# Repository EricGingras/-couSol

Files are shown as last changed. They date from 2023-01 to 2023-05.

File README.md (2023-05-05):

# Écou-Terre

**Déscription du projet:** Nous sommes en train de concevoir un module qui peut capter les bruits émis par les vers de terre, offrant ainsi une perspective sur la biodiversité et la santé des sols.  Ceci est le répertoire git de tous les fichiers techniques pour notre projet.

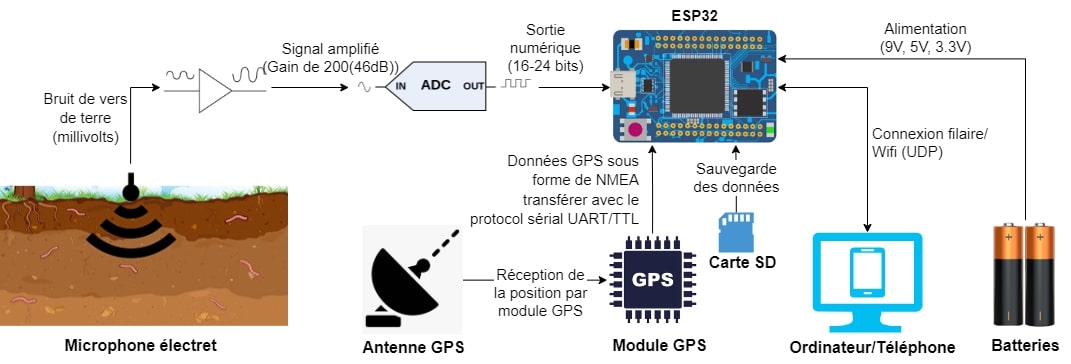
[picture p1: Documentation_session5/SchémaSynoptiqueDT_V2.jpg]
Schéma Synoptique


**Déscription technique:** Nous utilisons un microphone électret pour capter le bruit des vers de terre. Ce signal est ensuite amplifié et numérisé pour pouvoir le transmettre dans un ESP-32 en format I2S. Par la suite, ces données I2S sont enregistrées dans une carte SD en format WAV, ce qui permet ensuite de les écouter sur un ordinateur. Il y a aussi un connecteur jack 3,5mm pour l'écoute en temps réelle des vers de terre. Éventuellement, nous souhaitons ajouter un module GPS pouvant indiquer la position géographique de tous les échantillons sonores prélevés. Le module au complet est alimenté par une pile 4.2 volts. Pour le contrôler, nous allons avoir un page web avec un interface pour le démarrage, l'ârret et d'autre fonctions du module.

# Fichiers
> Déscription des fichiers dans le répertoire git.
- **3d_print:** Contient les fichiers pour la seule impression 3d que nous avons fait pour notre projet à date: une base pour le boîtier.
- **Documentation_pieces:** Contient tous les fichiers de documentation pour les pièces principales qui se retrouvent sur le module.
- **Documentation_session5:** Contient des fichiers de la session passée qui servent encore pour notre projet.
- **Fichier_PCB:** Contient tous les fichiers KiCad pour les PCB.
- **Prog_ESP-32:** Contient le code pour l'enregistrement des données I2S qui utilisait ESP-IDF ainsi que le code pour le serveur web qui servira à contrôler le module.

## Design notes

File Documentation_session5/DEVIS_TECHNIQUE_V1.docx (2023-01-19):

Devis technique

Pour le projet

Opération vers de terre

Présenté à CRIFA

par Jacob Turcotte et Eric Gingras

Remis

19 décombre 2022

# Mise en contexte

L’industrialisation du domaine agricole apporte plusieurs enjeux écologiques. Notamment, la diminution de la biodiversité dans la terre qui affecte directement l’absorption de l’eau dans le sol et la santé des plantes. Or, le CRIFA n’a pas de dispositif qui leur permet d’observer la biodiversité des sols. Des chercheurs suisses ont été capable d’utiliser un capteur qui leurs permettent de faire de l’écoute acoustique des sols. L’appareil leur permet d’écouter les insectes, comme les vers de terre, qui si trouve. Ils font du bruit en bougeant la terre autours d’eux, or ils peuvent entendre ce bruit avec l’appareil. Grâce à cette écoute, les chercheurs peuvent faire des comparaisons entre différents sols ainsi que des estimer de populations. Le CRIFA veut eux aussi avoir accès à un dispositif qui leur permettra de faire de l’écoute des sols du Québec et c’est notre tâche d’en faire la conception.

# Schéma synoptique

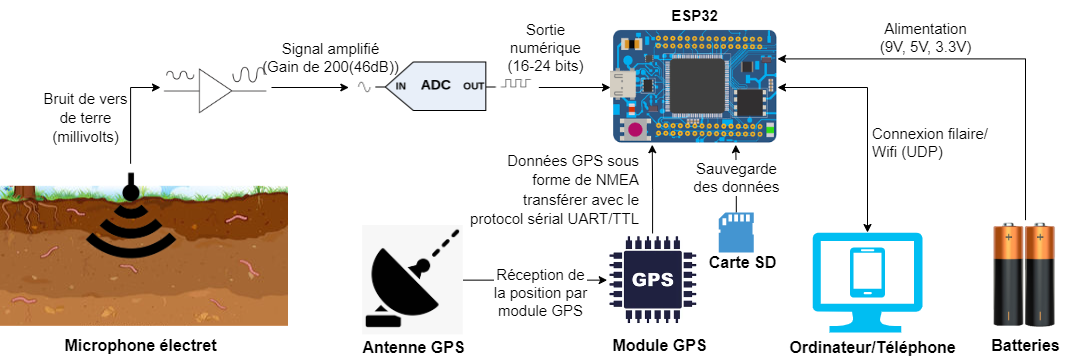
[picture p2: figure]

Figure 1 : Schéma synoptique

# Explication du schéma :

Quand le microphone électret est inséré dans le sol, il capte les vibrations des vers de terre. Le signal résultant est en millivolts et a besoin d’amplification pour être utile. Après l’amplification, le signal est transformé en numérique avec un convertisseur analogique à numérique pour ensuite être sauvegardé dans une carte SD. En même temps, un module GPS enregistre la position géographique où l’échantillon des vers de terre a été prélevé et l’envoie à la carte SD. Cette carte peut ensuite être branchée dans un ordinateur pour visualiser les données. La programmation du module se fera soit par connexion filaire ou par WiFi (UDP). Le circuit au complet sera alimenté par des batteries qui fourniront un signal de 9 Volts pour alimenter l’amplificateur. Il y aura aussi des régulateurs de tension de 3.3 Volts et de 5 Volts pour alimenter l’ESP32, le convertisseur analogique à numérique et le module GPS.

# Prototype, résultats déjà obtenus

Nous avons fait quelques tests préliminaires avec un module piézoélectrique, un amplificateur INA118 et un bocal de terre.

- Meilleur résultat:
  - Piezo collé sur une des parois de vitre du bocal. Capable de détecter le mouvement d'un crayon dans la terre.
- Pire résultat:
  - Sonde "guitare", beaucoup trop de bruit, pas capable de définir le signal reçu. On ne va pas refaire de test avec cette sonde.
- Résultat avec potentiel:
  - Tige de fil de métal soudé sur le piezo. Le fil que l’on a choisi était trop mince et trop flexible et atténuait les vibrations dans le sol. Cependant, la sonde créée par la compagnie suisse, Sounding Soil, utilise une tige de cuivre de 1mm de diamètre. Leur sonde est fonctionnelle, or nous devons essayer de la répliquer.

# Défis technique/risques

- Défis techniques
  - Avoir des résultats
    - Explication: La lecture d’acoustique dans le sol n’est pas facile. La terre est un excellent isolant, or, si cette terre est sèche, le bruit ne se propage vraiment pas bien. C’est pour cette raison qu’un sol humide est beaucoup plus facile à écouter. Néanmoins cela reste un défi, même si on demande à l’usager d’arroser le sol avant l’utilisation.
    - Risque associé: Si on n'est pas capable d’avoir de résultats, nous n’avons simplement pas de projet. Le prototype va vraiment nous dire si cela est possible ou non.
  - Avoir des lectures avec une bonne qualité numérique
    - Explication: L’enregistrement de son audible est un défi. Il nous faut des convertisseurs analogiques à numériques (CAN) assez rapide, ainsi qu’une définition assez haute.
    - Risque associé: Si on n'est pas capable d’avoir de belles données une fois sur portable, le son sera horrible et les analyses de ces données ne seront pas bonnes non plus.
  - Traitement des résultats
    - Explication: Le CAN va envoyer énormément de données au ESP-32. Or, le programme et le ESP-32 doivent être capables de traiter l’information rapidement sans erreurs.
    - Risque associé: Si on n'est pas capable de faire le traitement des données assez rapidement, il a de fortes possibilités de perdre les futures mesures.
  - Sauvegarder les données dans une carte SD
    - Explication: L’enregistrement des données dans une carte SD nous apporte plusieurs avantages, notamment la facilitation de l’envoi de ces données dans un ordinateur et sécurité que toutes les données sont enregistrées (limitation de perte de donnée par Wi-Fi).
    - Risque associé: Le ESP-32 peut interfacer avec une carte SD, mais ce n’est pas évident. Sans cette fonctionnalité, certaines données pourraient être perdues par une mauvaise connexion Wi-Fi.

# Schéma électrique

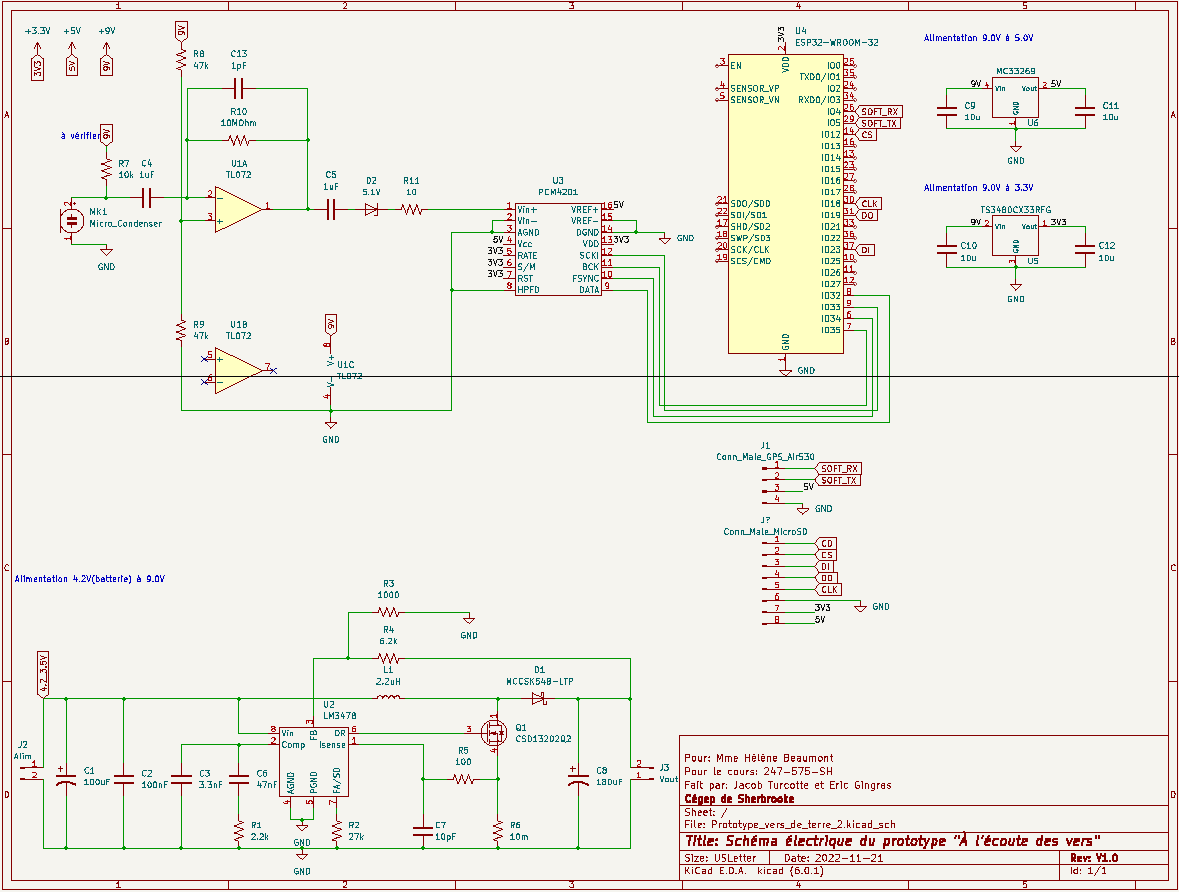
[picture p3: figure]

D)

C)

A)

B)

Figure 2: Schéma électrique

Je vais expliquer le schéma électrique en section.

A) Le microphone électret a besoin d’une source pour bien marcher. Le microphone fonctionne comme un condensateur. Or, lorsqu’il y’a du bruit l’une des parois du condensateur bouge ce qui entraîne un changement de charge que l’on peut mesurer. Le condensateur C4 est l’a pour créer un filtre passe haut. R7 et C13 sont là pour rajouter de la stabilité au système ainsi que de réduire le bruit provenant de l’ampli. L’amplificateur opérationnel (U1) est configuré en mode Différentiateur, ainsi Vout=-RC(dVin)/(dt) . Nous voulons avoir une tension de sortie de 0 à 5V. Le micro que on utilise à une sensibilité de -38dB. Or, -38dB=10^(-38/20) qui donne 0.0125V/Pa. Nous n’avons pas trouvé de mesure pour le son produit d’un vers de terre, cependant la voix humaine est en moyenne à 60dB, ainsi 60dB=10^(60/20) *20μPa qui donne 0.02Pa (20μPa est le point de référence pour l’oreille humaine à 1000Hz). Or, le microphone à une plage de 0 à 25mV. Ce qui veut dire que nous avons besoin d’un gain de 200. Or, avec un condensateur de 1μF nous avons besoin d’une résistance de 10MOhm(R10). Le condensateur C5 est là pour enlever le décalage sortant de l’amplificateur afin d’avoir un 0 à 5V. La diode Zener (D2) et R11 sert à protéger le CAN au cas où que la tension dépasserait les 5V. Le CAN (U3) marche avec deux tensions. 5V pour le côté analogique et 3.3V pour le côté numérique. Ceci est parfait pour nous puisque que le ESP-32(U4) fonctionne avec une source 3.3V. Le CAN crée un format numérique PCM (pulse-code modulation) qui sera géré par le ESP-32 en I2S. Le CAN aura une définition numérique de 24bit et un taux d’échantillonnage ajustable pouvant aller à 108kHz.
B) Cette section représente le ESP-32(U4) et les pins du module GPS Air530(J1). Le ESP-32 communiquera avec le module GPS avec une communication série logiciel (soft serial). Il communiquera avec le CAN(U3) en I2S. On pourra s’y connecter avec un ordinateur sois par port série ou bien par UDP(Wifi). Il y’aura aussi une carte microSD où nous allons pouvoir y enregistrer toutes les données accumulées.
C) Cette section contient les régulateurs 3.3V et 5V. Ils reçoivent tous les deux une tension de 9V venant de l’alimentation de découplage (U2) dans la section D. Les tensions 3.3V et 5V seront utilisées afin d’alimenter toutes les composantes (à l’exception de l’amplificateur opérationnel (U1)).
D) Cette section représente l’alimentation par découplage recommandé par Webench de Texas Instrument. Elle nous permettra d’avoir une batterie rechargeable de 4.2V qui nous fournira une tension de 9V. Cette tension de 9V sera utilisée par les régulateurs de tension ainsi que l’amplificateur opérationnel (U1).

# Évaluation des coûts

*Les items en double sont là au cas où nous endommageons la pièce pendant la soudure ou lors de test

**ceci est un estimer des coûts, il va changer au fils du projet

Nom | Numéros pièce | Fournisseur(s) et lien(s) internet(s) | Description | Nombre de pièce voulu | Prix d’une pièce
TL072 | TL072ACPS-ND | Digikey TL072ACPS Texas Instruments | Integrated Circuits (ICs) | DigiKey (https://www.digikey.ca/en/products/detail/texas-instruments/TL072ACPS/9692585) | Amplificateurs opérationnels | 2 | 23.86$
PCM4201PW | 595-PCM4201PW | Mouser PCM4201PW Texas Instruments | Mouser Canada (https://www.mouser.ca/ProductDetail/Texas-Instruments/PCM4201PW?qs=wgAEGBTxy7kg7qu2mYKbqg%3D%3D) | CAN (Convertisseur Analogique à Numérique) audio | 2 | 8.72$
109020022 | 713-109020022 | Mouser 109020022 Seeed Studio | Mouser Canada (https://www.mouser.ca/ProductDetail/Seeed-Studio/109020022?qs=7MVldsJ5Uaxl%2Fe3vvm7cBA%3D%3D) | Module GPS | 1 | 18.08$
SanDisk Ultra SDSQUNS-016G-GN3MN 16GB 80MB/s UHS-I Class 10 microSDHC Card | B074B4P7KD | Amazon SanDisk Ultra SDSQUNS-016G-GN3MN 16GB 80MB/s UHS-I Class 10 microSDHC Card : Amazon.ca: Electronics (https://www.amazon.ca/gp/product/B074B4P7KD/ref=ewc_pr_img_1?smid=A2U7BYCM1HXLY3&psc=1) | Carte micro-SD | 1 | 10.59$
MicroSD card breakout board+ | 254 | Adafruit MicroSD card breakout board+ : ID 254 : $7.50 : Adafruit Industries, Unique & fun DIY electronics and kits (https://www.adafruit.com/product/254) | Module carte micro-SD | 1 | 7.50$
ESP-32S ESP-WROOM-32 | ‎WYTP66-CA | Amazon WayinTop 2pcs WiFi Development Board for ESP32 ESP-32S ESP-WROOM-32 2.4 GHz Dual Cores WLAN WiFi + Bluetooth 38 Pin Microcontroller + 1M Micro USB Cable for Arduino IDE : Amazon.ca: Electronics (https://www.amazon.ca/gp/product/B086ZMDB7H/ref=ewc_pr_img_1?smid=A22PZZC3JNHS9L&psc=1) | Microcontrô-leur | 1 | 29.99$
Piezoélectrique | B087P25FRC | Amazon 20 PCS 27mm Piezo Element Piezo Pickup Guitar Pickup Transducer for Acoustic Guitar Ukulele : Amazon.ca: Musical Instruments, Stage & Studio (https://www.amazon.ca/gp/product/B087P25FRC/ref=ox_sc_act_title_1?smid=A1JJ30UPYWSO06&psc=1) | Élément Piezo | 1 | 15.99$
MC33269DR2G | 863-MC33269DR2G | Mouser MC33269DR2G onsemi | Mouser Canada (https://www.mouser.ca/ProductDetail/?qs=OSf9jACorvY6DAHklU91Yg%3D%3D) | Convertisseur 9V à 5V | 2 | 1.15$
TS3480CX33RFG | 821-TS3480CX33RFG | Mouser TS3480CX33 RFG Taiwan Semiconductor | Mouser Canada (https://www.mouser.ca/ProductDetail/Taiwan-Semiconductor/TS3480CX33-RFG?qs=QEzMiVqgwc2c0RrRJ9G0kw%3D%3D) | Convertisseur 9V à 3.3V | 2 | 0.98$
PCB | | JLCPCB PCB Order & Online PCB Quote & PCB Assembly Quote - JLCPCB (https://cart.jlcpcb.com/quote?orderType=1&stencilLayer=2&stencilWidth=100&stencilLength=100&stencilCounts=5) | PCB avec dimension de 10 par 10 cm | 3 | 30$
Boitier | | | Boitier fait à partir des imprimantes 3d du cégep | 3 | 10$
NCR18650B | NCR18650B | Flashlightworld Panasonic NCR18650B Flat Top Battery - FlashlightWorld — FlashLightWorld Canada (https://www.flashlightworld.ca/products/panasonic-ncr18650b-battery-3-6v-18650-flat-top-battery) | Batterie | 2 | 21.99$
Transport | | Tous | | (5x JLCPCB, Mouser, Digikey, Adafruit) | 30$
Total: | | | | | 423.67$

# Échéancier

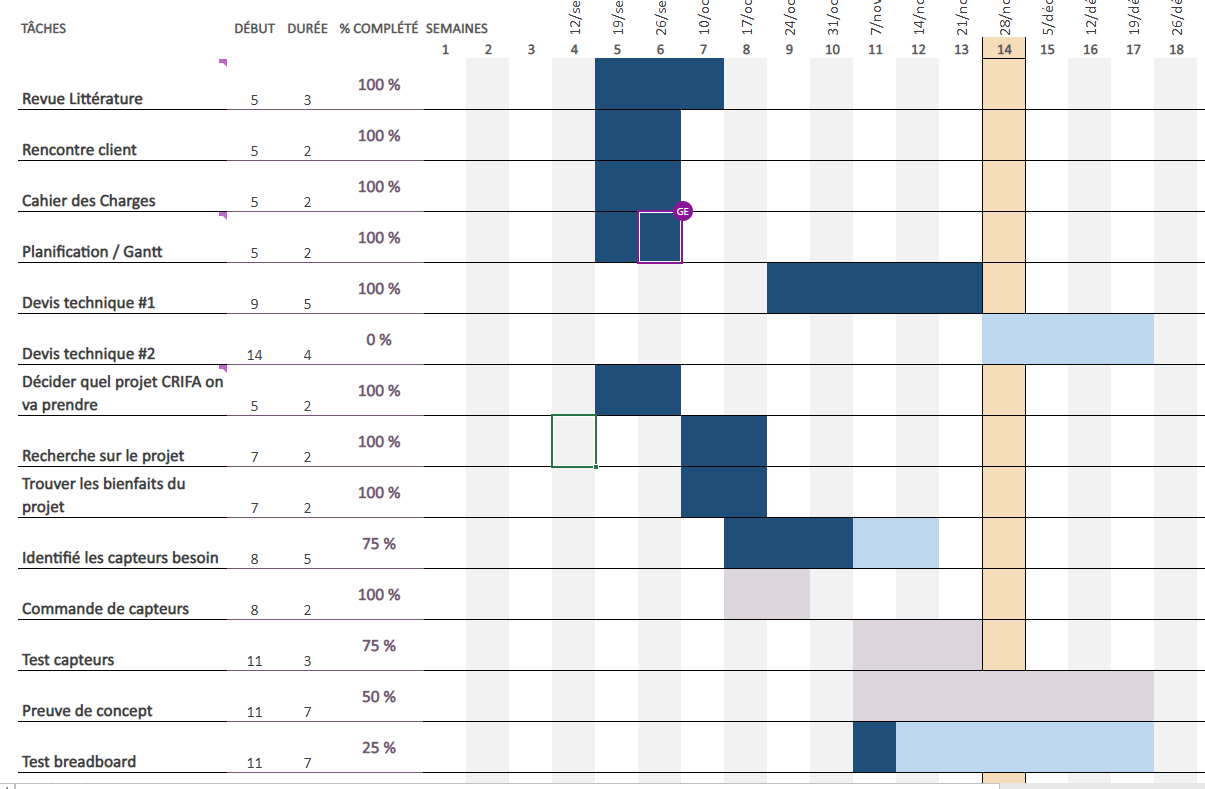
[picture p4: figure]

# Interface usager

- Interface principale :

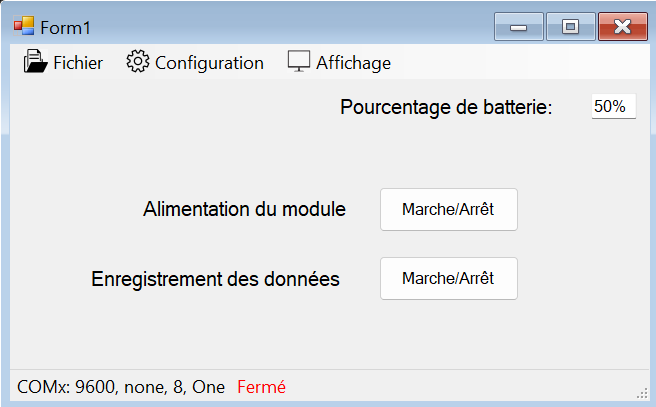
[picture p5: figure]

- Interface pour la communication série :

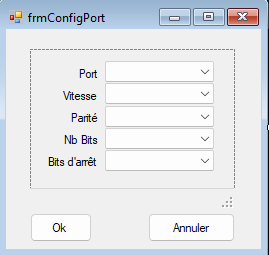
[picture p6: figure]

- L’écran pour l’affichage des données.

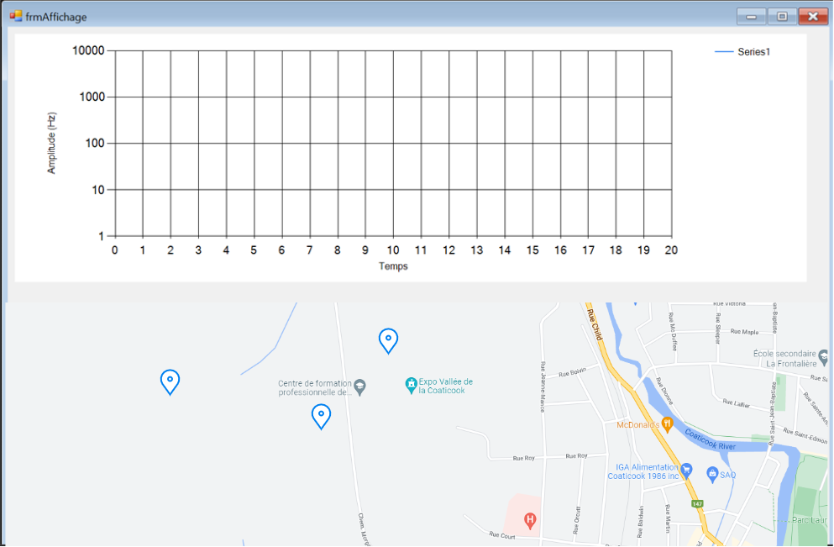
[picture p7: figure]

Points enregistrés

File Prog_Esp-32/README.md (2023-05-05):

# ÉcouTerre/Prog_Esp-32

## Contient la majorité du code pour le Esp32

### ***NE PAS OUBLIER: tout le code dans ce répertoire a besoin des librairies eps-idf.***

 1. Esp_PA_WEB
	 - Contient le code nécessaire pour que l'ESP-32 marche en Point d'Accès (PA) et qu'il gère son propre serveur Web.
 2. test_I2S_GPT
	 - Contient le code que l'on utilise afin de tester le protocole I2S ainsi que la sauvegarde des données dans la carte microSD. 
 3. i2s_record_final
	 - Contient le code que l'on utilise dans la version final du produit. Il gère l'enregistrement avec l'aide d'un bouton

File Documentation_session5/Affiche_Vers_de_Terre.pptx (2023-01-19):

## À l’écoute des vers

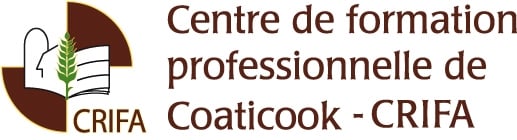
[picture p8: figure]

- Capter les vibrations des insectes (notamment les vers de terres) dans le sol.
- Enregistrement des données et de la position GPS sur carte SD.
- Créer un produit qui pourrait aider à sensibiliser les gens à
l’importance de la biodiversité des sols.

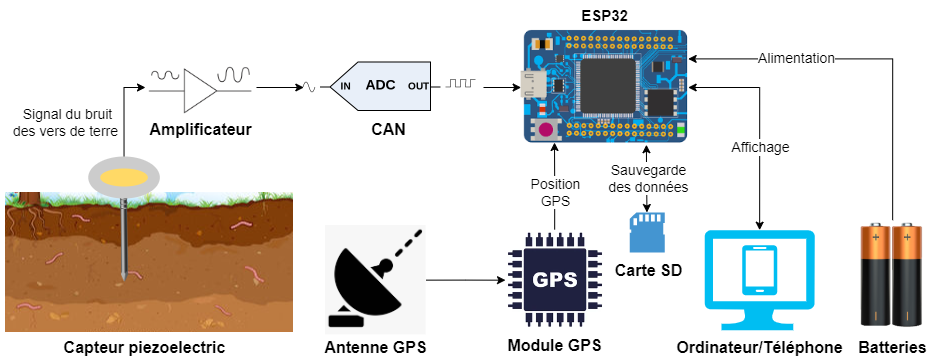
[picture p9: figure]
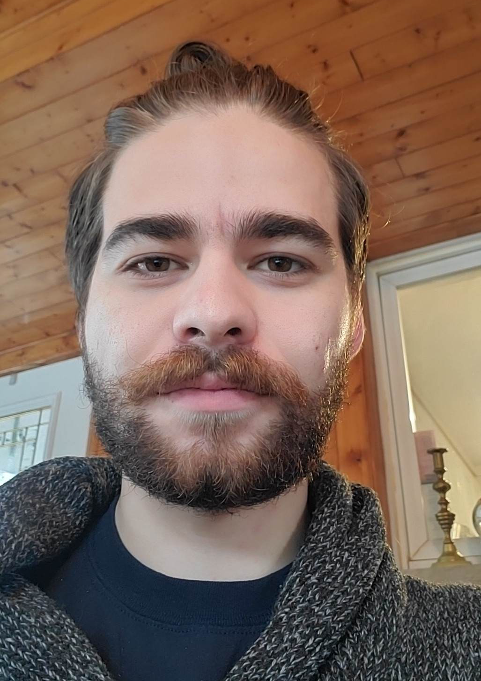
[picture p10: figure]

Jacob Turcotte

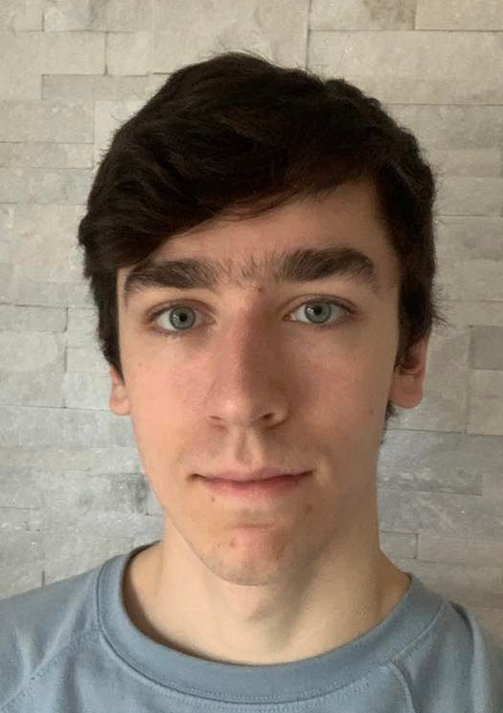
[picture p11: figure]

Eric Gingras

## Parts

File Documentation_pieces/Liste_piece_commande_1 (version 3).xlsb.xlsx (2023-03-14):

Nombre de pièce: | Description de la pièce | Nom pièce magasin | Magasin | Lien | Coût | Total
6 | Diode zener SMT 5.1V | MMSZ5231B-7-F | Digikey | https://www.digikey.ca/en/products/detail/diodes-incorporated/MMSZ5231B-7-F/755472 | 0.24 | 1.44
3 | Condensateur 0.022uF SMT 805 | CGA4J3X7R2E223K125AA | Digikey | https://www.digikey.ca/en/products/detail/tdk-corporation/CGA4J3X7R2E223K125AA/2443314 | 0.32 | 0.96
3 | Ampli. Opp. TL072 | TL072HIDDFR | Digikey | TL072HIDDFR Texas Instruments | Integrated Circuits (ICs) | DigiKey (https://www.digikey.ca/en/products/detail/texas-instruments/TL072HIDDFR/14641418) | 0.79 | 2.37
3 | Condensateur 470uF SMT | A768KS477M1CLAE017 | Digikey | A768KS477M1CLAE017 KEMET | Capacitors | DigiKey (https://www.digikey.ca/en/products/detail/kemet/A768KS477M1CLAE017/13420066) | 1.37 | 4.11
5 | Ampli. Opp. audio pour speaker | LM386MMX-1/NOPB | Digikey | LM386MMX-1/NOPB Texas Instruments | Integrated Circuits (ICs) | DigiKey (https://www.digikey.ca/en/products/detail/texas-instruments/LM386MMX-1-NOPB/367095) | 2.53 | 12.65
3 | Ampli. Opp. audio pour micro OPA1652 | OPA1652AIDRGT | Digikey | https://www.digikey.ca/en/products/detail/texas-instruments/OPA1652AIDRGT/8106013 | 4.22 | 12.66
2 | Connecteur 3.5mm audio mono | MJ-3523-SMT-TR | Digikey | MJ-3523-SMT-TR CUI Devices | Connectors, Interconnects | DigiKey (https://www.digikey.ca/en/products/detail/cui-devices/MJ-3523-SMT-TR/281296) | 1.46 | 2.92
5 | ADC audio 2 channel I2S | PCM1804DB | Digikey | PCM1804DB Texas Instruments | Integrated Circuits (ICs) | DigiKey (https://www.digikey.ca/en/products/detail/texas-instruments/PCM1804DB/431985) | 11.68 | 58.4

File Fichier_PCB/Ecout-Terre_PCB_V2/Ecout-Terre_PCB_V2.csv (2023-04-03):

Ref | Qnty | Value | Cmp name | Footprint
C1, C2, C5, C6, | 4 | 10u | C | Capacitor_SMD:C_0805_2012Metric_Pad1.18x1.45mm_HandSolder
C3, C10, | 2 | 180uF | C_Polarized_US | Capacitor_SMD:CP_Elec_6.3x9.9
C4, C14, C17, C29, C30, C31, C32, C33, C34, C40, C42, | 11 | 0.1uF | C | Capacitor_SMD:C_0805_2012Metric_Pad1.18x1.45mm_HandSolder
C7, | 1 | 3300pF | C | Capacitor_SMD:C_0805_2012Metric_Pad1.18x1.45mm_HandSolder
C8, | 1 | 56nF | C | Capacitor_SMD:C_0504_1310Metric_Pad0.83x1.28mm_HandSolder
C9, C18, C24, | 3 | 10pF | C | Capacitor_SMD:C_0805_2012Metric_Pad1.18x1.45mm_HandSolder
C11, C12, C13, C16, C39, C41, C43, C44, | 8 | 1uF | C | Capacitor_SMD:C_0805_2012Metric_Pad1.18x1.45mm_HandSolder
C15, | 1 | 2.2uF | C | Capacitor_SMD:C_0805_2012Metric_Pad1.18x1.45mm_HandSolder
C19, C21, | 2 | 0.022uF | C | Capacitor_SMD:C_0805_2012Metric_Pad1.18x1.45mm_HandSolder
C20, | 1 | 22nF | C | Capacitor_SMD:C_0805_2012Metric_Pad1.18x1.45mm_HandSolder
C22, | 1 | 3.3uF | C_Polarized_US | Capacitor_SMD:C_0805_2012Metric_Pad1.18x1.45mm_HandSolder
C23, C27, C28, C35, C36, | 5 | 10uF | C_Polarized | Capacitor_SMD:C_0805_2012Metric_Pad1.18x1.45mm_HandSolder
C25, | 1 | 0.047uF | C | Capacitor_SMD:C_0805_2012Metric_Pad1.18x1.45mm_HandSolder
C26, | 1 | 470uF | C_Polarized_US | Capacitor_SMD:C_Elec_8x10.2
C37, C38, | 2 | 20pF | C | Capacitor_SMD:C_0805_2012Metric_Pad1.18x1.45mm_HandSolder
D1, | 1 | MCCSK54B-LTP | D_Schottky | Diode_SMD:D_SMB
D2, D3, D4, D5, | 4 | D_Z_2V4 | D_Zener | Diode_SMD:D_SOD-123
D6, | 1 | DEL_5V | LED | LED_SMD:LED_0805_2012Metric_Pad1.15x1.40mm_HandSolder
D7, | 1 | DEL_3V3 | LED | LED_SMD:LED_0805_2012Metric_Pad1.15x1.40mm_HandSolder
J1, | 1 | USB_C_Receptacle_USB2.0 | USB_C_Receptacle_USB2.0 | Connector_USB:USB_C_Receptacle_HRO_TYPE-C-31-M-12
J2, | 1 | Pile | Screw_Terminal_01x02 | TerminalBlock:TerminalBlock_bornier-2_P5.08mm
J3, | 1 | AudioJack4 | AudioJack4 | Connector_Audio:Jack_3.5mm_CUI_SJ-3524-SMT_Horizontal
J4, | 1 | Test_5V | Conn_01x02_Male | Connector_PinHeader_2.54mm:PinHeader_1x02_P2.54mm_Vertical
J5, | 1 | Conn_Alim | Screw_Terminal_01x04 | TerminalBlock:TerminalBlock_bornier-4_P5.08mm
J6, | 1 | Test_3V3 | Conn_01x02_Male | Connector_PinHeader_2.54mm:PinHeader_1x02_P2.54mm_Vertical
J7, J8, | 2 | Conn_ESP | Conn_01x19_Female | Connector_PinSocket_2.54mm:PinSocket_1x19_P2.54mm_Vertical
J9, | 1 | Sortie_alim | Screw_Terminal_01x04 | TerminalBlock:TerminalBlock_bornier-4_P5.08mm
J10, | 1 | Micro_SD_Card | Micro_SD_Card | Connector_Card:microSD_HC_Wuerth_693072010801
J11, | 1 | Test_10V | Conn_01x02_Male | Connector_PinHeader_2.54mm:PinHeader_1x02_P2.54mm_Vertical
J12, | 1 | Conn_01x01_Male | Conn_01x01_Male | Connector_PinSocket_2.54mm:PinSocket_1x01_P2.54mm_Vertical
J13, | 1 | Conn_GPS | Conn_01x04_Male | Connector_PinSocket_2.00mm:PinSocket_1x04_P2.00mm_Vertical
J14, | 1 | Conn_Audio_Alim | Conn_01x02_Female | Connector_Wire:SolderWire-0.75sqmm_1x02_P4.8mm_D1.25mm_OD2.3mm
J15, | 1 | Conn_Audio_Diff | Conn_01x02_Female | Connector_Wire:SolderWire-0.75sqmm_1x02_P4.8mm_D1.25mm_OD2.3mm
J16, | 1 | Conn_Main_Alim | Conn_01x02_Female | Connector_Wire:SolderWire-0.75sqmm_1x02_P4.8mm_D1.25mm_OD2.3mm
J17, | 1 | Conn_Main_Diff | Conn_01x02_Female | Connector_Wire:SolderWire-0.75sqmm_1x02_P4.8mm_D1.25mm_OD2.3mm
J18, | 1 | Conn_01x03_Male | Conn_01x03_Male | Connector_PinHeader_2.54mm:PinHeader_1x03_P2.54mm_Vertical
L1, | 1 | 3.3uH | L | Inductor_SMD:L_Vishay_IHLP-4040
MK1, | 1 | Micro | Microphone_Condenser | Connector_Wire:SolderWire-0.1sqmm_1x02_P3.6mm_D0.4mm_OD1mm
Q1, | 1 | CSD16327Q3 | CSD16327Q3 | Package_SON:VSON-8_3.3x3.3mm_P0.65mm_NexFET
R1, | 1 | 2.2k | R_US | Resistor_SMD:R_0805_2012Metric
R2, | 1 | 27k | R_US | Resistor_SMD:R_0805_2012Metric
R3, | 1 | 1000 | R_US | Resistor_SMD:R_0805_2012Metric
R4, | 1 | 6.8k | R_US | Resistor_SMD:R_0805_2012Metric
R5, | 1 | 100 | R_US | Resistor_SMD:R_0805_2012Metric
R6, | 1 | 8m | R_US | Resistor_SMD:R_0815_2038Metric_Pad1.20x4.05mm_HandSolder
R7, R8, R9, R10, R11, R22, R23, R24, R25, R26, R27, R28, R29, R30, R31, R32, R33, R37, R38, | 19 | 10k | R_US | Resistor_SMD:R_0805_2012Metric_Pad1.20x1.40mm_HandSolder
R12, | 1 | 1M | R_US | Resistor_SMD:R_0805_2012Metric_Pad1.20x1.40mm_HandSolder
R13, | 1 | 75k | R_US | Resistor_SMD:R_0805_2012Metric_Pad1.20x1.40mm_HandSolder
R14, R16, | 2 | 47k | R_US | Resistor_SMD:R_0805_2012Metric_Pad1.20x1.40mm_HandSolder
R15, R17, | 2 | 120 | R_US | Resistor_SMD:R_0805_2012Metric_Pad1.20x1.40mm_HandSolder
R18, | 1 | 470 | R_US | Resistor_SMD:R_0805_2012Metric_Pad1.20x1.40mm_HandSolder
R19, | 1 | 330 | R_US | Resistor_SMD:R_0805_2012Metric_Pad1.20x1.40mm_HandSolder
R20, | 1 | 10 | R_US | Resistor_SMD:R_0805_2012Metric_Pad1.20x1.40mm_HandSolder
R21, | 1 | 1k | R_US | Resistor_SMD:R_0805_2012Metric_Pad1.20x1.40mm_HandSolder
R34, R35, | 2 | 2.2k | R_US | Resistor_SMD:R_0805_2012Metric_Pad1.20x1.40mm_HandSolder
R36, | 1 | 680 | R_US | Resistor_SMD:R_0805_2012Metric_Pad1.20x1.40mm_HandSolder
R39, | 1 | 9.1k | R_US | Resistor_SMD:R_0805_2012Metric_Pad1.20x1.40mm_HandSolder
R40, | 1 | 1.25k | R_US | Resistor_SMD:R_0805_2012Metric_Pad1.20x1.40mm_HandSolder
RV1, | 1 | 10k | R_Potentiometer_US | Potentiometer_THT:Potentiometer_Bourns_3386P_Vertical
RV2, | 1 | 100k | R_Potentiometer_US | Potentiometer_SMD:Potentiometer_Bourns_TC33X_Vertical
U1, | 1 | TS3480CX33RFG | TS3480CX33RFG | Package_TO_SOT_SMD:SOT-23
U2, | 1 | MC33269 | MC33269 | Package_SO:SO-8_3.9x4.9mm_P1.27mm
U3, | 1 | LM3478 | LM3478 | Package_SO:SOIC-8_3.9x4.9mm_P1.27mm
U4, | 1 | PCM1804 | PCM1804 | Package_SO:SSOP-28_5.3x10.2mm_P0.65mm
U5, U8, | 2 | OPA1656 | TL072 | Package_SO:SOIC-8_3.9x4.9mm_P1.27mm
U6, | 1 | LM386 | LM386 | Package_SO:SOIC-8_3.9x4.9mm_P1.27mm
U7, | 1 | 74LVT04 | 74HC04 | Package_SO:SOIC-14_3.9x8.7mm_P1.27mm
Y1, | 1 | 7V-22.5792MAHV-T | Crystal | Crystal:Crystal_SMD_3225-4Pin_3.2x2.5mm

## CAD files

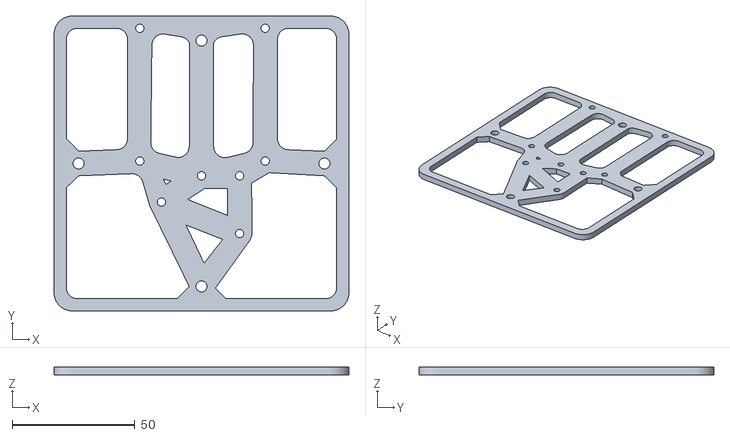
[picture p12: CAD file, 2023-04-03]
3d_print/boitierv1 v2.stl
120.0 x 120.0 x 3.30

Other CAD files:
3d_print/Base_v1_boitier.f3d

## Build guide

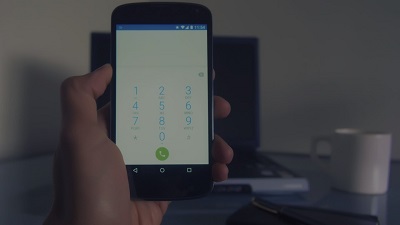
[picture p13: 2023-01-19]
Documentation_pieces/ESP32_MicroSD/ESP32_ Guide for MicroSD Card Module Arduino _ Random Nerd Tutorials_files/home-automation-sb-img.jpg

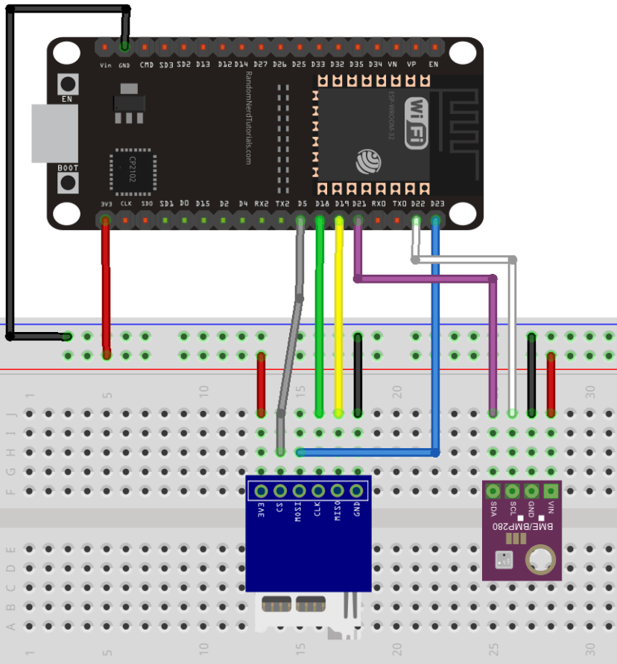
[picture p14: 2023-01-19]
Documentation_pieces/ESP32_MicroSD/ESP32_ Guide for MicroSD Card Module Arduino _ Random Nerd Tutorials_files/ESP32-microSD-card-BME280-circuit-diagram.png

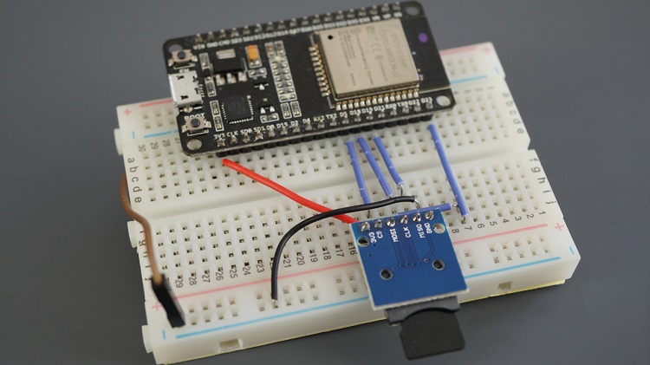
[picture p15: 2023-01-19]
Documentation_pieces/ESP32_MicroSD/ESP32_ Guide for MicroSD Card Module Arduino _ Random Nerd Tutorials_files/ESP32-microSD-card-module-wiring-breadboard.jpg

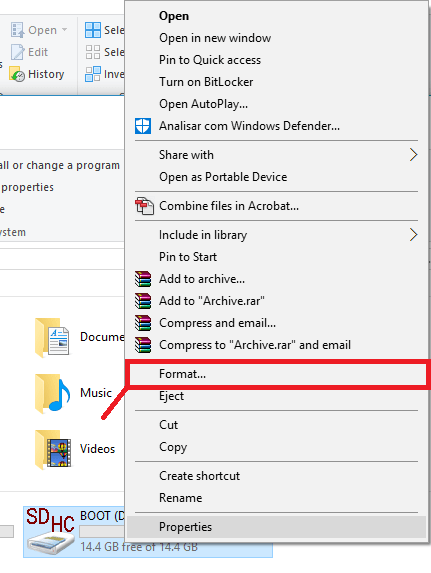
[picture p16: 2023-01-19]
Documentation_pieces/ESP32_MicroSD/ESP32_ Guide for MicroSD Card Module Arduino _ Random Nerd Tutorials_files/format-SD-card-1.png

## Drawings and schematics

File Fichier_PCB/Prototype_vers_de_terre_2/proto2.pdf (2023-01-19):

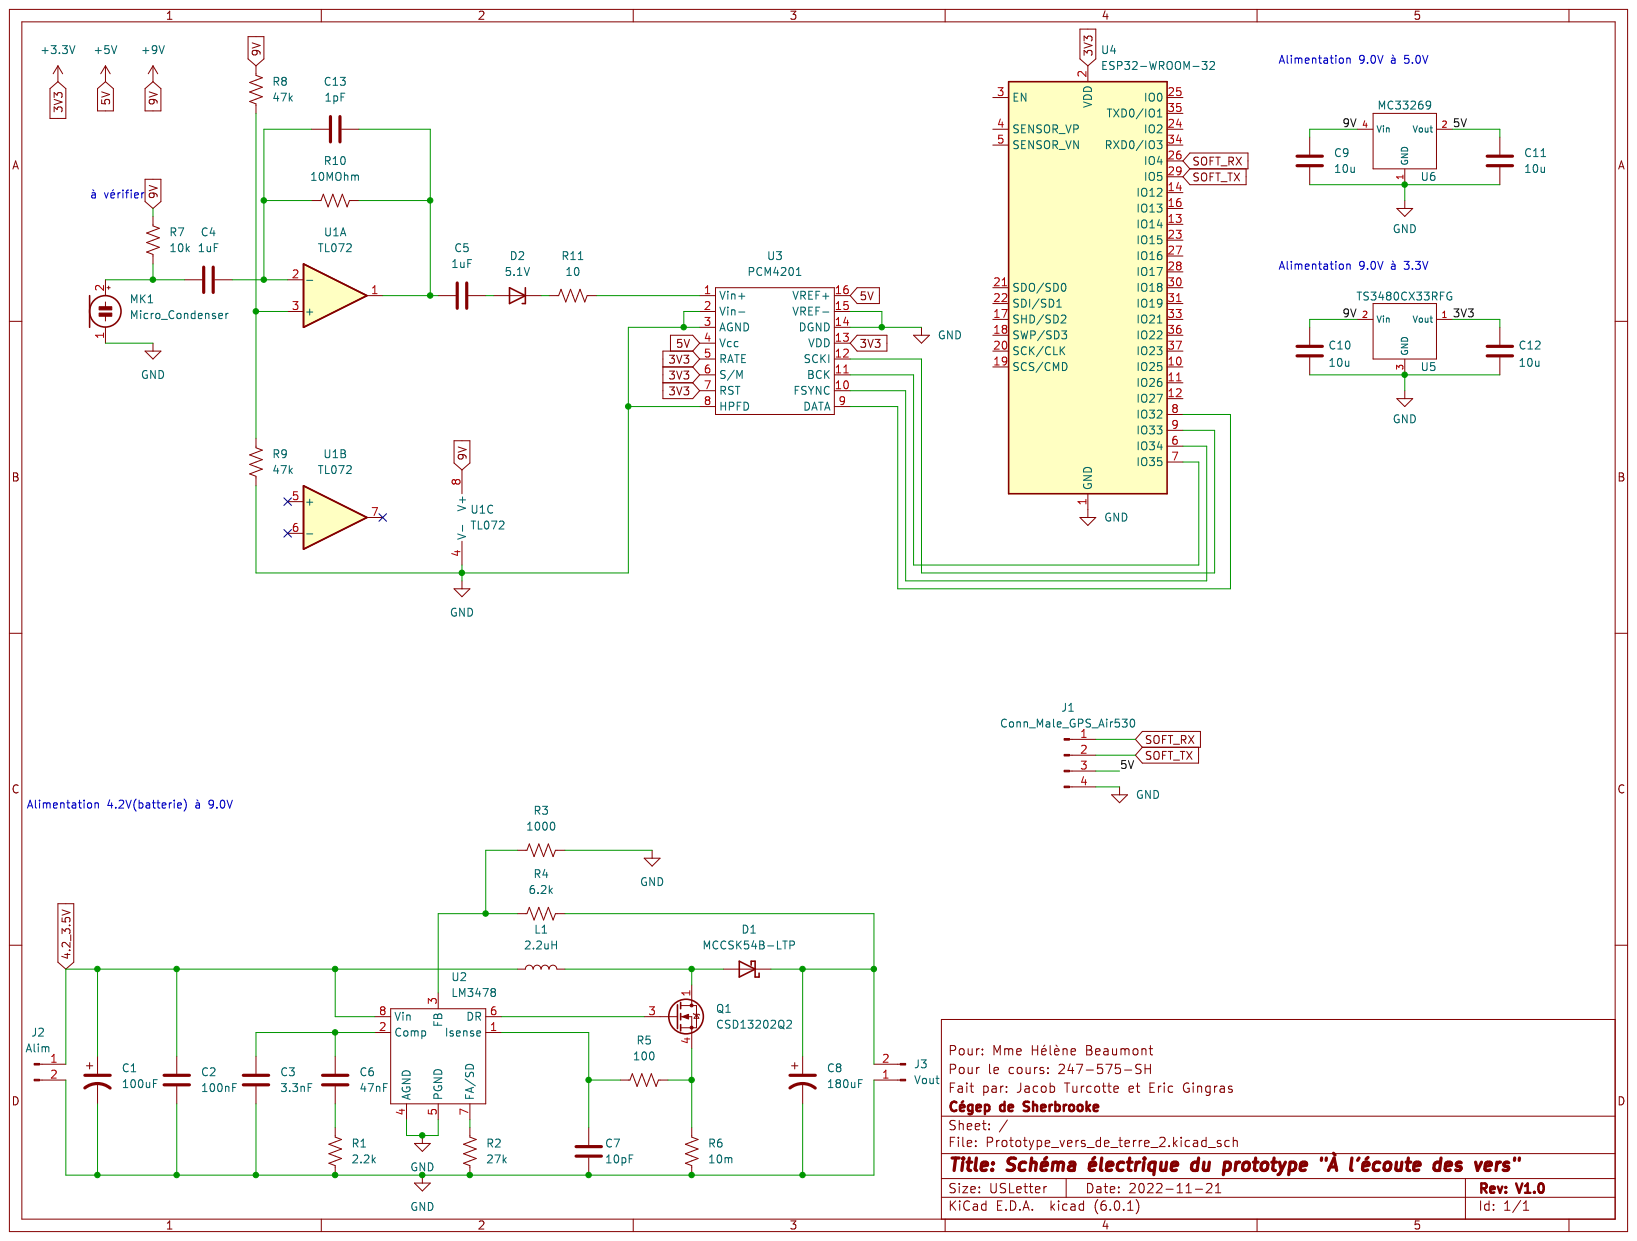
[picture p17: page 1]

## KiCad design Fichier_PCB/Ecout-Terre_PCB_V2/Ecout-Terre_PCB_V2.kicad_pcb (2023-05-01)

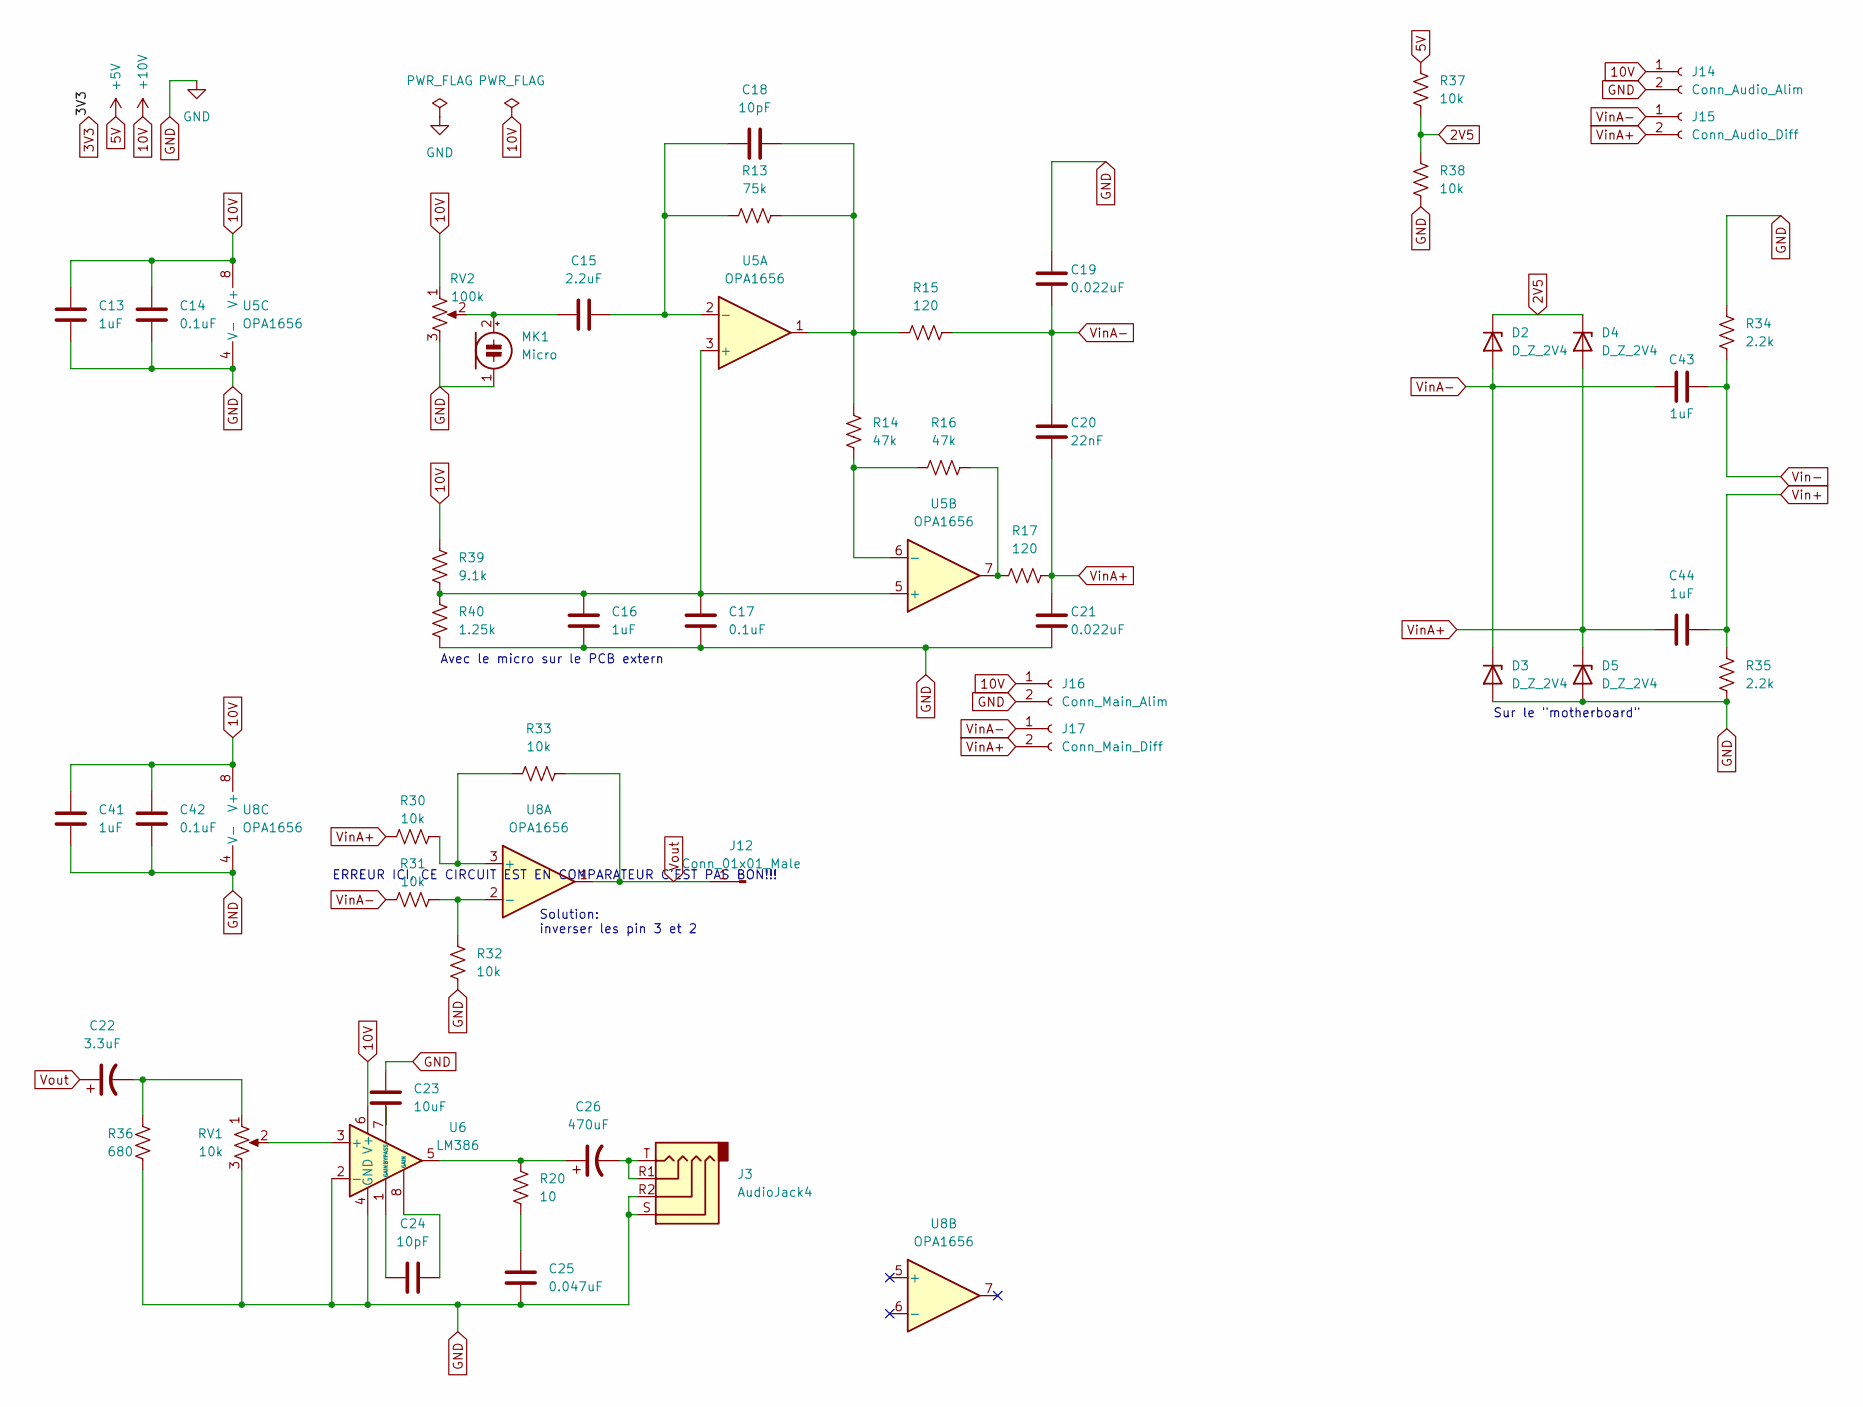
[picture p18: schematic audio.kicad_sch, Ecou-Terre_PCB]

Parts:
C13, C16, C41, C43, C44: 1uF; C_0805_2012Metric_Pad1.18x1.45mm_HandSolder
C14, C17, C42: 0.1uF; C_0805_2012Metric_Pad1.18x1.45mm_HandSolder
C15: 2.2uF; C_0805_2012Metric_Pad1.18x1.45mm_HandSolder
C18, C24: 10pF; C_0805_2012Metric_Pad1.18x1.45mm_HandSolder
C19, C21: 0.022uF; C_0805_2012Metric_Pad1.18x1.45mm_HandSolder
C20: 22nF; C_0805_2012Metric_Pad1.18x1.45mm_HandSolder
C22: 3.3uF; C_0805_2012Metric_Pad1.18x1.45mm_HandSolder
C23: 10uF; C_0805_2012Metric_Pad1.18x1.45mm_HandSolder
C25: 0.047uF; C_0805_2012Metric_Pad1.18x1.45mm_HandSolder
C26: 470uF; C_Elec_8x10.2
D2, D3, D4, D5: D_Z_2V4; D_SOD-123
J3: AudioJack4; Jack_3.5mm_CUI_SJ-3524-SMT_Horizontal
J12: Conn_01x01_Male; PinSocket_1x01_P2.54mm_Vertical
J14: Conn_Audio_Alim; SolderWire-0.75sqmm_1x02_P4.8mm_D1.25mm_OD2.3mm
J15: Conn_Audio_Diff; SolderWire-0.75sqmm_1x02_P4.8mm_D1.25mm_OD2.3mm
J16: Conn_Main_Alim; SolderWire-0.75sqmm_1x02_P4.8mm_D1.25mm_OD2.3mm
J17: Conn_Main_Diff; SolderWire-0.75sqmm_1x02_P4.8mm_D1.25mm_OD2.3mm
MK1: Micro; SolderWire-0.1sqmm_1x02_P3.6mm_D0.4mm_OD1mm
R13: 75k; R_0805_2012Metric_Pad1.20x1.40mm_HandSolder
R14, R16: 47k; R_0805_2012Metric_Pad1.20x1.40mm_HandSolder
R15, R17: 120; R_0805_2012Metric_Pad1.20x1.40mm_HandSolder
R20: 10; R_0805_2012Metric_Pad1.20x1.40mm_HandSolder
R30, R31, R32, R33, R37, R38: 10k; R_0805_2012Metric_Pad1.20x1.40mm_HandSolder
R34, R35: 2.2k; R_0805_2012Metric_Pad1.20x1.40mm_HandSolder
R36: 680; R_0805_2012Metric_Pad1.20x1.40mm_HandSolder
R39: 9.1k; R_0805_2012Metric_Pad1.20x1.40mm_HandSolder
R40: 1.25k; R_0805_2012Metric_Pad1.20x1.40mm_HandSolder
RV1: 10k; Potentiometer_Bourns_3386P_Vertical
RV2: 100k; Potentiometer_Bourns_TC33X_Vertical
U5, U8: OPA1656; SOIC-8_3.9x4.9mm_P1.27mm
U6: LM386; SOIC-8_3.9x4.9mm_P1.27mm

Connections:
2V5: D2.1 (K), D4.1 (K), R37.1, R38.2
5V: R37.2; also elsewhere on the board
10V: C13.2, C14.2, C41.2, C42.2, J14.1, J16.1, R39.1, RV2.1, U5.8 (V+), U6.6 (V+), U8.8 (V+); also elsewhere on the board
GND: C13.1, C14.1, C16.1, C17.1, C19.2, C21.1, C23.1, C25.2, C41.1, C42.1, D3.2 (A), D5.2 (A), J3.R2, J3.S, J3.TN, J14.2, J16.2, MK1.1 (-), R32.1, R34.1, R35.2, R36.1, R38.1, R40.2, RV1.3, RV2.3, U5.4 (V-), U6.2 (-), U6.4 (GND), U8.4 (V-); also elsewhere on the board
unnamed: C15.1, MK1.2 (+), RV2.2
unnamed: C15.2, C18.1, R13.1, U5.2 (-)
unnamed: C16.2, C17.2, R39.2, R40.1, U5.3 (+), U5.5 (+)
unnamed: C18.2, R13.2, R14.1, R15.1, U5.1
unnamed: C22.2, R36.2, RV1.1
unnamed: C23.2, U6.7 (BYPASS)
unnamed: C24.1, U6.1 (GAIN)
unnamed: C24.2, U6.8 (GAIN)
unnamed: C25.1, R20.2
unnamed: C26.1, R20.1, U6.5
unnamed: C26.2, J3.R, J3.R1, J3.T
unnamed: R14.2, R16.1, U5.6 (-)
unnamed: R16.2, R17.1, U5.7
unnamed: R30.2, R33.1, U8.3 (+)
unnamed: R31.2, R32.2, U8.2 (-)
unnamed: RV1.2, U6.3 (+)
Vin+: C44.1, R35.1; also elsewhere on the board
Vin-: C43.1, R34.2; also elsewhere on the board
VinA+: C20.1, C21.2, C44.2, D4.2 (A), D5.1 (K), J15.2, J17.2, R17.2, R30.1
VinA-: C19.1, C20.2, C43.2, D2.2 (A), D3.1 (K), J15.1, J17.1, R15.2, R31.1
Vout: C22.1, J12.1, R33.2, U8.1

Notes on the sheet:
Solution: inverser les pin 3 et 2
ERREUR ICI, CE CIRCUIT EST EN COMPARATEUR C'EST PAS BON!!!
Sur le "motherboard"
Avec le micro sur le PCB extern

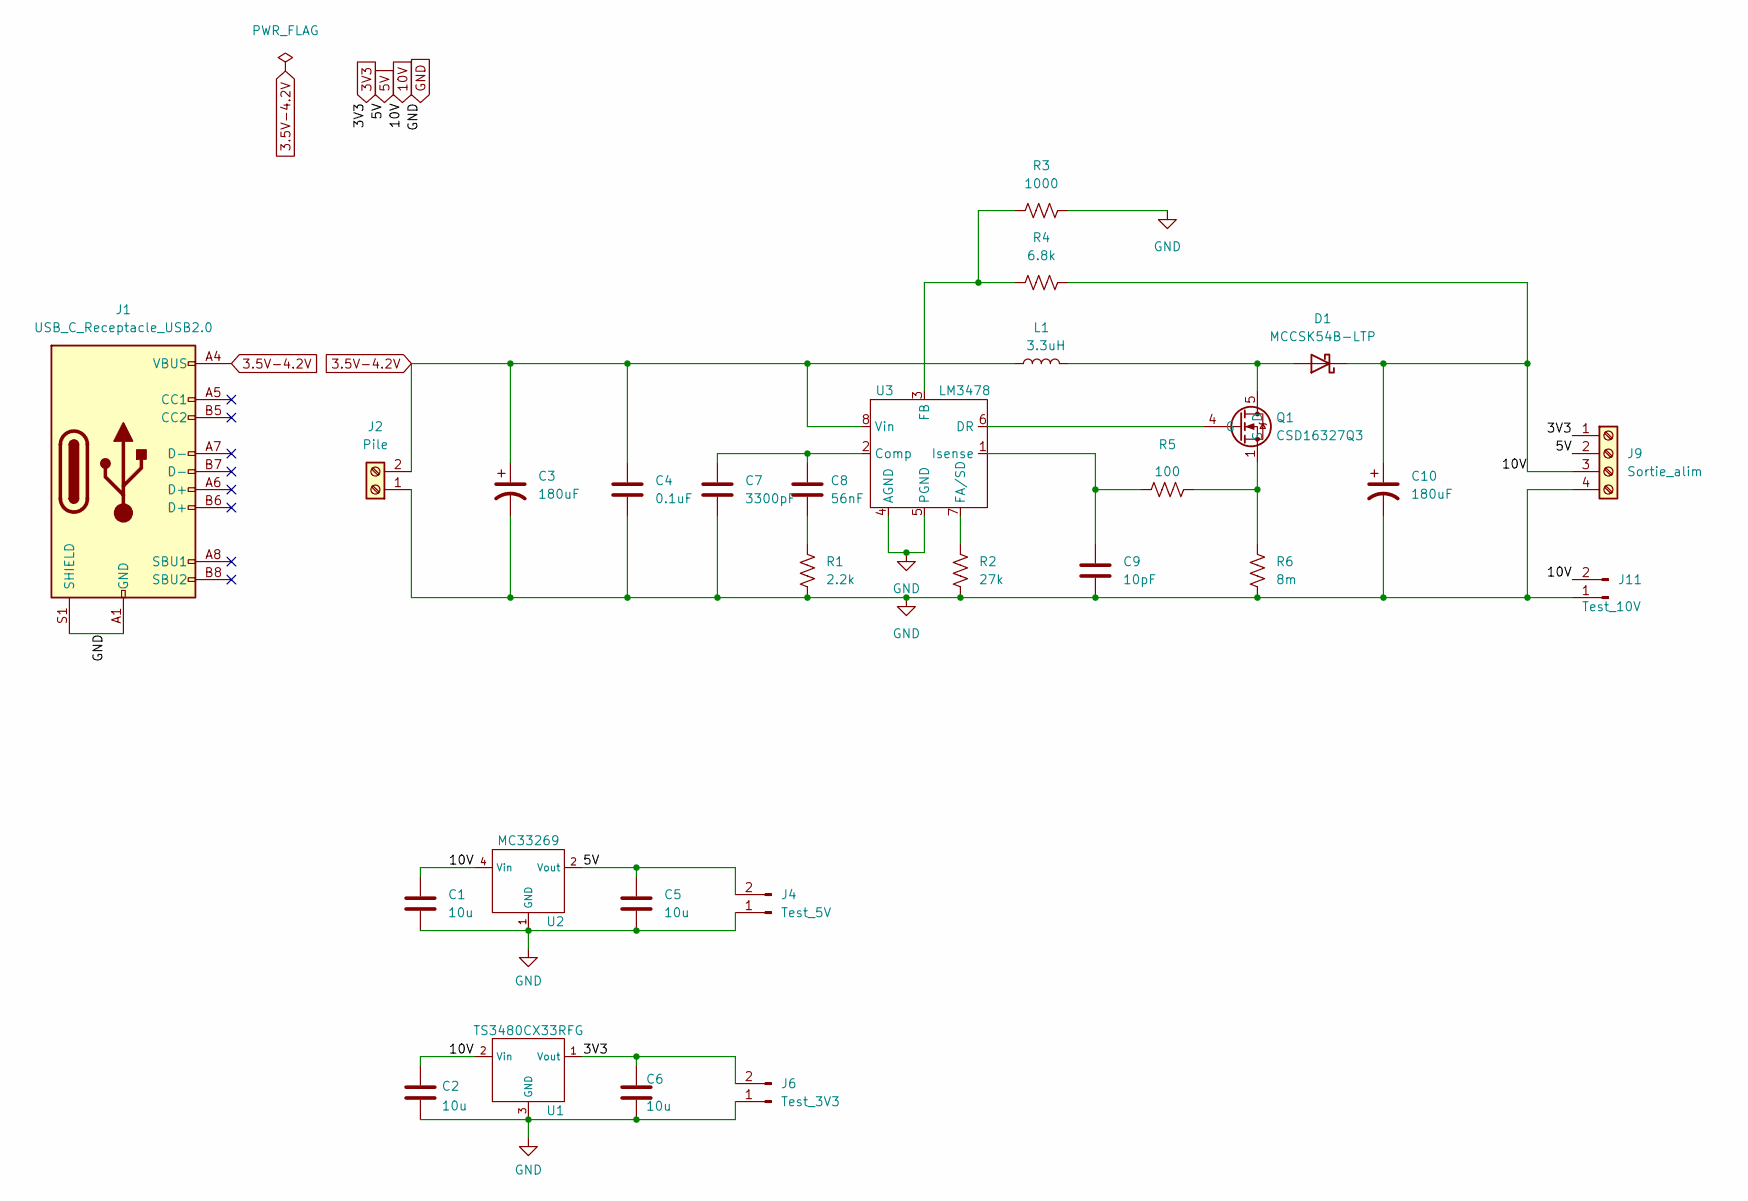
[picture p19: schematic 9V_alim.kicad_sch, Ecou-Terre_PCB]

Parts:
C1, C2, C5, C6: 10u; C_0805_2012Metric_Pad1.18x1.45mm_HandSolder
C3, C10: 180uF; CP_Elec_6.3x9.9
C4: 0.1uF; C_0805_2012Metric_Pad1.18x1.45mm_HandSolder
C7: 3300pF; C_0805_2012Metric_Pad1.18x1.45mm_HandSolder
C8: 56nF; C_0504_1310Metric_Pad0.83x1.28mm_HandSolder
C9: 10pF; C_0805_2012Metric_Pad1.18x1.45mm_HandSolder
D1: MCCSK54B-LTP; D_SMB
J1: USB_C_Receptacle_USB2.0; USB_C_Receptacle_HRO_TYPE-C-31-M-12
J2: Pile; TerminalBlock_bornier-2_P5.08mm
J4: Test_5V; PinHeader_1x02_P2.54mm_Vertical
J6: Test_3V3; PinHeader_1x02_P2.54mm_Vertical
J9: Sortie_alim; TerminalBlock_bornier-4_P5.08mm
J11: Test_10V; PinHeader_1x02_P2.54mm_Vertical
L1: 3.3uH; L_Vishay_IHLP-4040
Q1: CSD16327Q3; VSON-8_3.3x3.3mm_P0.65mm_NexFET
R1: 2.2k; R_0805_2012Metric
R2: 27k; R_0805_2012Metric
R3: 1000; R_0805_2012Metric
R4: 6.8k; R_0805_2012Metric
R5: 100; R_0805_2012Metric
R6: 8m; R_0815_2038Metric_Pad1.20x4.05mm_HandSolder
U1: TS3480CX33RFG; SOT-23
U2: MC33269; SO-8_3.9x4.9mm_P1.27mm
U3: LM3478; SOIC-8_3.9x4.9mm_P1.27mm

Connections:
3.5V-4.2V: C3.1, C4.1, J1.A4 (VBUS), J1.A9 (VBUS), J1.B4 (VBUS), J1.B9 (VBUS), J2.2, L1.1, U3.8 (Vin)
3V3: C6.1, J6.2, J9.1, U1.1 (Vout); also elsewhere on the board
5V: C5.1, J4.2, J9.2, U2.2 (Vout), U2.3 (Vout), U2.6 (Vout), U2.7 (Vout); also elsewhere on the board
10V: C1.1, C2.1, C10.1, D1.1 (K), J9.3, J11.2, R4.2, U1.2 (Vin), U2.4 (Vin); also elsewhere on the board
GND: C1.2, C2.2, C3.2, C4.2, C5.2, C6.2, C7.2, C9.2, C10.2, J1.A1 (GND), J1.A12 (GND), J1.B1 (GND), J1.B12 (GND), J1.S1 (SHIELD), J2.1, J4.1, J6.1, J9.4, J11.1, R1.2, R2.2, R3.2, R6.1, U1.3 (GND), U2.1 (GND), U3.4 (AGND), U3.5 (PGND); also elsewhere on the board
unnamed: C7.1, C8.1, U3.2 (Comp)
unnamed: C8.2, R1.1
unnamed: C9.1, R5.1, U3.1 (Isense)
unnamed: D1.2 (A), L1.2, Q1.5 (D)
unnamed: Q1.1 (S), Q1.2 (S), Q1.3 (S), R5.2, R6.2
unnamed: Q1.4 (G), U3.6 (DR)
unnamed: R2.1, U3.7 (FA/SD)
unnamed: R3.1, R4.1, U3.3 (FB)

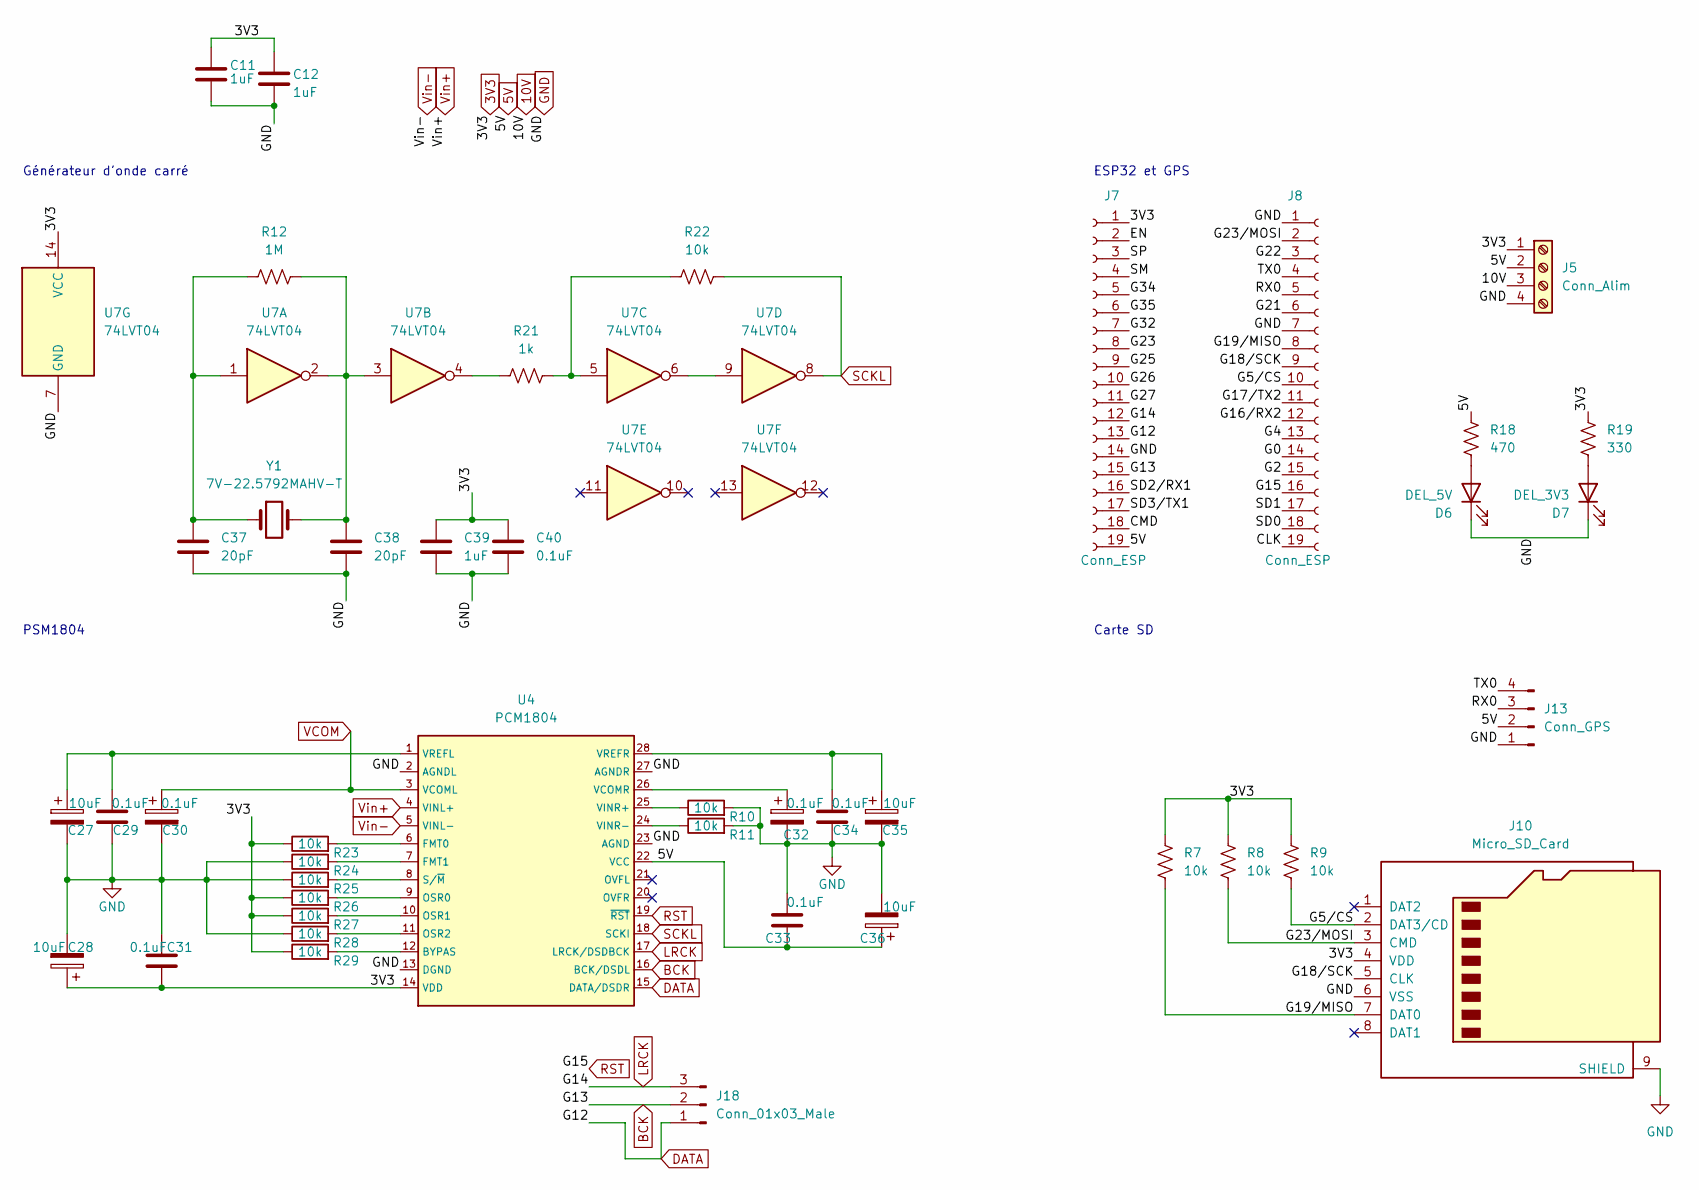
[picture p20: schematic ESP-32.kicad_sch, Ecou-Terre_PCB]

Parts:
C11, C12, C39: 1uF; C_0805_2012Metric_Pad1.18x1.45mm_HandSolder
C27, C28, C35, C36: 10uF; C_0805_2012Metric_Pad1.18x1.45mm_HandSolder
C29, C30, C31, C32, C33, C34, C40: 0.1uF; C_0805_2012Metric_Pad1.18x1.45mm_HandSolder
C37, C38: 20pF; C_0805_2012Metric_Pad1.18x1.45mm_HandSolder
D6: DEL_5V; LED_0805_2012Metric_Pad1.15x1.40mm_HandSolder
D7: DEL_3V3; LED_0805_2012Metric_Pad1.15x1.40mm_HandSolder
J5: Conn_Alim; TerminalBlock_bornier-4_P5.08mm
J7, J8: Conn_ESP; PinSocket_1x19_P2.54mm_Vertical
J10: Micro_SD_Card; microSD_HC_Wuerth_693072010801
J13: Conn_GPS; PinSocket_1x04_P2.00mm_Vertical
J18: Conn_01x03_Male; PinHeader_1x03_P2.54mm_Vertical
R7, R8, R9, R10, R11, R22, R23, R24, R25, R26, R27, R28, R29: 10k; R_0805_2012Metric_Pad1.20x1.40mm_HandSolder
R12: 1M; R_0805_2012Metric_Pad1.20x1.40mm_HandSolder
R18: 470; R_0805_2012Metric_Pad1.20x1.40mm_HandSolder
R19: 330; R_0805_2012Metric_Pad1.20x1.40mm_HandSolder
R21: 1k; R_0805_2012Metric_Pad1.20x1.40mm_HandSolder
U4: PCM1804; SSOP-28_5.3x10.2mm_P0.65mm
U7: 74LVT04; SOIC-14_3.9x8.7mm_P1.27mm
Y1: 7V-22.5792MAHV-T; Crystal_SMD_3225-4Pin_3.2x2.5mm

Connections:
3V3: C11.1, C12.1, C28.1, C31.1, C39.1, C40.1, J5.1, J7.1, J10.4 (VDD), R7.1, R8.1, R9.1, R19.1, R23.1, R26.1, R27.1, R29.1, U4.14 (VDD), U7.14 (VCC); also elsewhere on the board
5V: C33.1, C36.1, J5.2, J7.19, J13.2, R18.1, U4.22 (VCC); also elsewhere on the board
10V: J5.3; also elsewhere on the board
/ESP-32/CLK: J8.19
/ESP-32/CMD: J7.18
/ESP-32/EN: J7.2
/ESP-32/G0: J8.14
/ESP-32/G2: J8.15
/ESP-32/G4: J8.13
/ESP-32/G5/CS: J8.10, J10.2 (DAT3/CD), R9.2
/ESP-32/G16/RX2: J8.12
/ESP-32/G17/TX2: J8.11
/ESP-32/G18/SCK: J8.9, J10.5 (CLK)
/ESP-32/G19/MISO: J8.8, J10.7 (DAT0), R7.2
/ESP-32/G21: J8.6
/ESP-32/G22: J8.3
/ESP-32/G23: J7.8
/ESP-32/G23/MOSI: J8.2, J10.3 (CMD), R8.2
/ESP-32/G25: J7.9
/ESP-32/G26: J7.10
/ESP-32/G27: J7.11
/ESP-32/G32: J7.7
/ESP-32/G34: J7.5
/ESP-32/G35: J7.6
/ESP-32/RX0: J8.5, J13.3
/ESP-32/SD0: J8.18
/ESP-32/SD1: J8.17
/ESP-32/SD2/RX1: J7.16
/ESP-32/SD3/TX1: J7.17
/ESP-32/SM: J7.4
/ESP-32/SP: J7.3
/ESP-32/TX0: J8.4, J13.4
BCK: J7.15, J18.2, U4.16 (BCK/DSDL)
DATA: J7.13, J18.1, U4.15 (DATA/DSDR)
GND: C11.2, C12.2, C27.2, C28.2, C29.1, C30.2, C31.2, C32.2, C33.2, C34.1, C35.2, C36.2, C37.2, C38.2, C39.2, C40.2, D6.1 (K), D7.1 (K), J5.4, J7.14, J8.1, J8.7, J10.6 (VSS), J10.9 (SHIELD), J13.1, R10.2, R11.2, R24.1, R25.1, R28.1, U4.2 (AGNDL), U4.13 (DGND), U4.23 (AGND), U4.27 (AGNDR), U7.7 (GND); also elsewhere on the board
LRCK: J7.12, J18.3, U4.17 (LRCK/DSDBCK)
unnamed: C27.1, C29.2, U4.1 (VREFL)
unnamed: C32.1, U4.26 (VCOMR)
unnamed: C34.2, C35.1, U4.28 (VREFR)
unnamed: C37.1, R12.1, U7.1, Y1.1
unnamed: C38.1, R12.2, U7.2, U7.3, Y1.2, Y1.3
unnamed: D6.2 (A), R18.2
unnamed: D7.2 (A), R19.2
unnamed: R10.1, U4.25 (VINR+)
unnamed: R11.1, U4.24 (VINR-)
unnamed: R21.1, U7.4
unnamed: R21.2, R22.1, U7.5
unnamed: R23.2, U4.6 (FMT0)
unnamed: R24.2, U4.7 (FMT1)
unnamed: R25.2, U4.8 (S/~M)
unnamed: R26.2, U4.9 (OSR0)
unnamed: R27.2, U4.10 (OSR1)
unnamed: R28.2, U4.11 (OSR2)
unnamed: R29.2, U4.12 (BYPAS)
unnamed: U7.6, U7.9
RST: J8.16, U4.19 (~RST)
SCKL: R22.2, U4.18 (SCKI), U7.8
VCOM: C30.1, U4.3 (VCOML)
Vin+: U4.4 (VINL+); also elsewhere on the board
Vin-: U4.5 (VINL-); also elsewhere on the board

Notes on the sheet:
ESP32 et GPS
Générateur d'onde carré
PSM1804
Carte SD

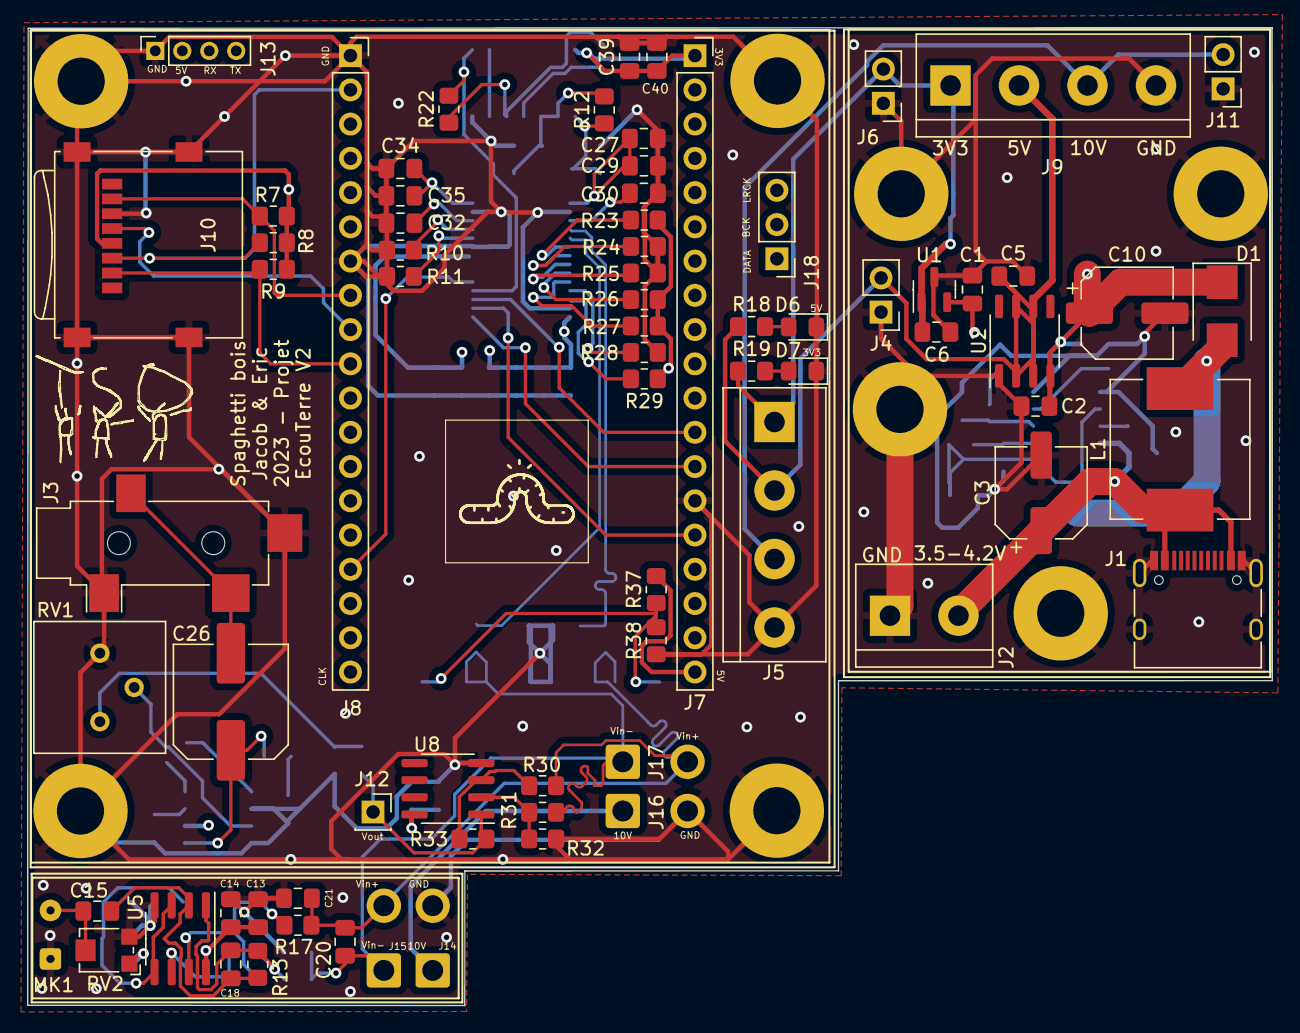
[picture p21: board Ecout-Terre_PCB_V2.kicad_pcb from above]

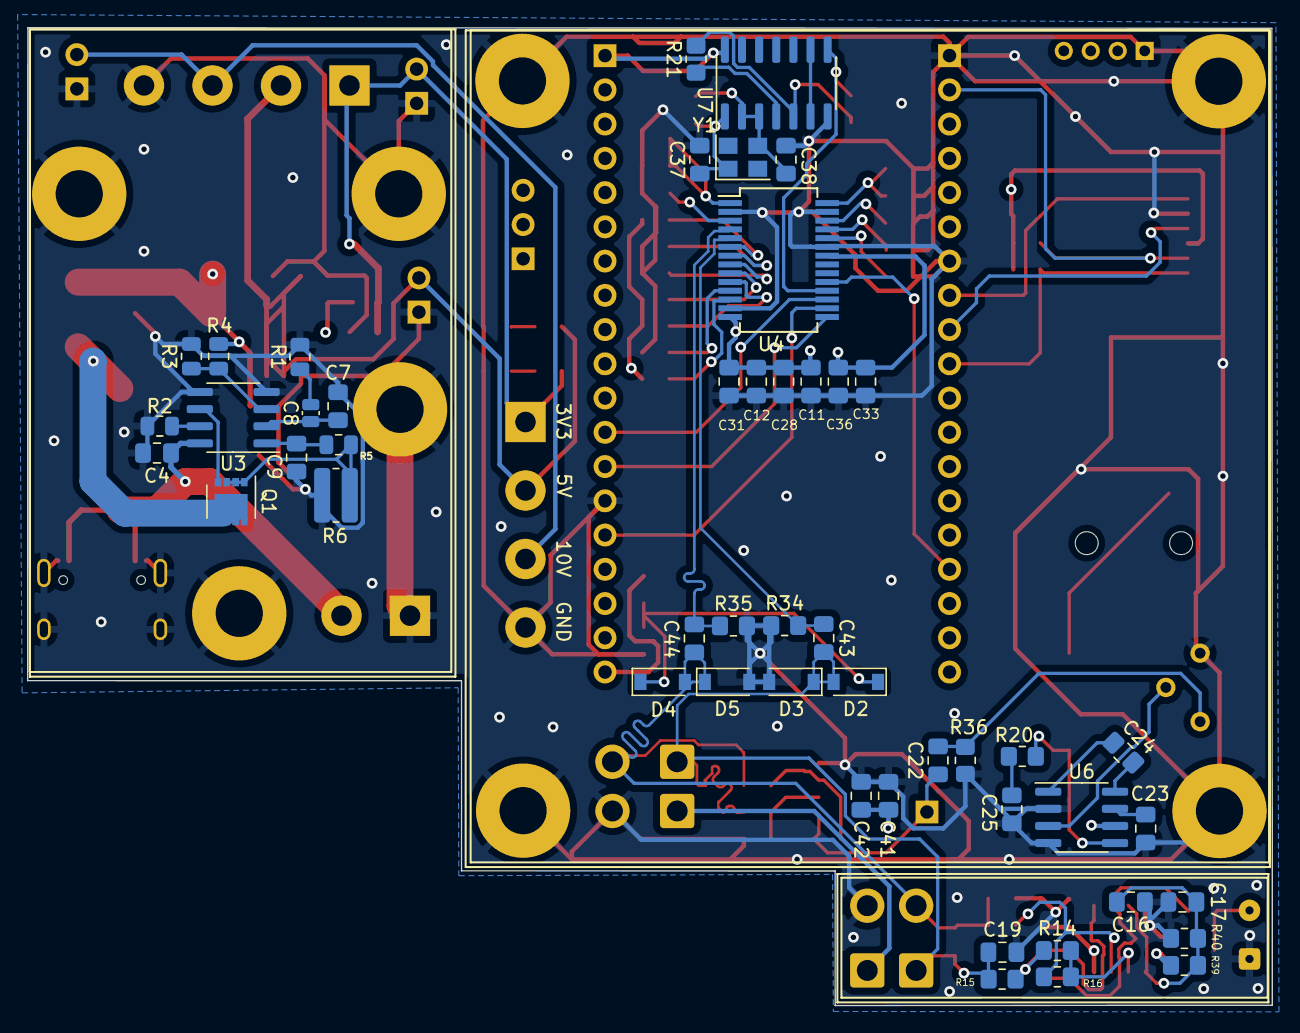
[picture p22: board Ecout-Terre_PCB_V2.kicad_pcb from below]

Board: 4 copper layers, 92.3 x 72.5 mm, 123 parts (49 on the bottom side), 66 nets.

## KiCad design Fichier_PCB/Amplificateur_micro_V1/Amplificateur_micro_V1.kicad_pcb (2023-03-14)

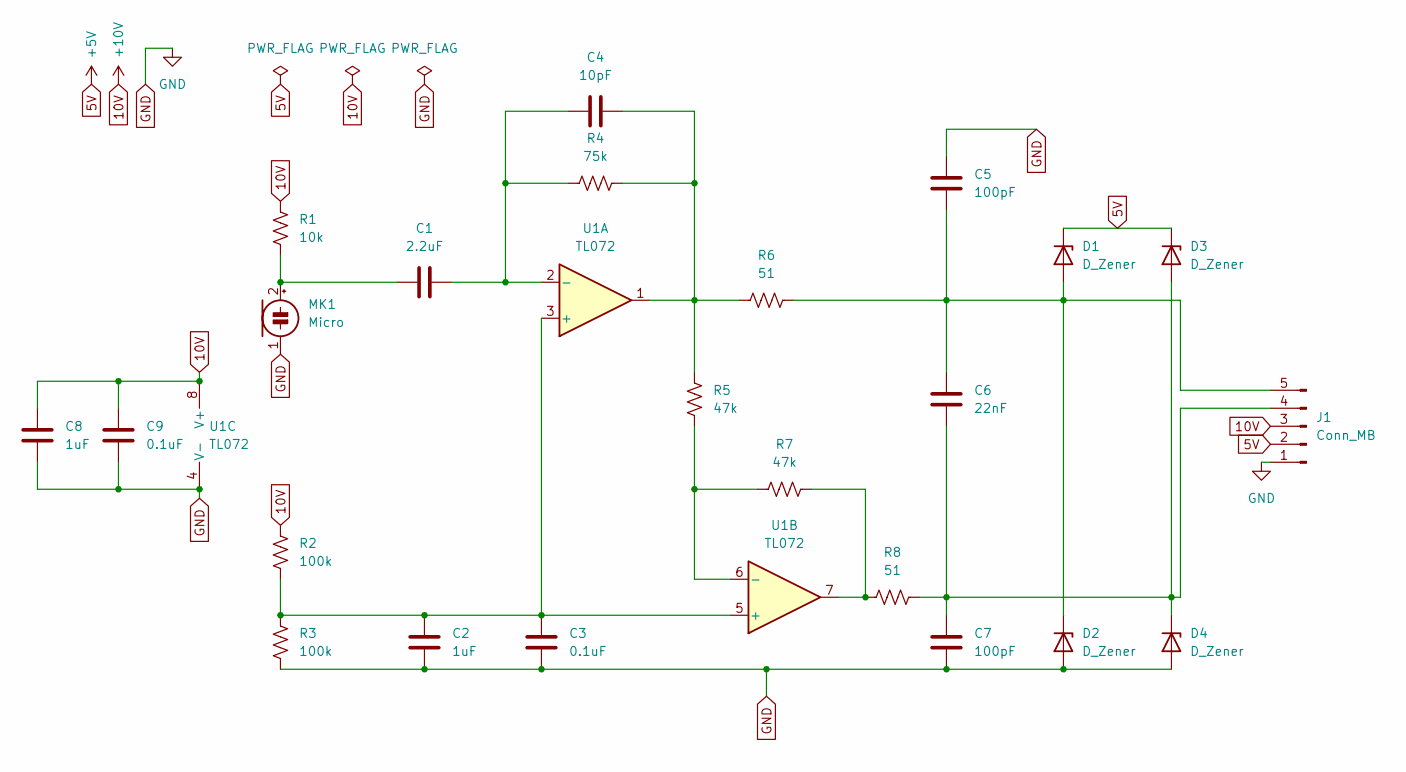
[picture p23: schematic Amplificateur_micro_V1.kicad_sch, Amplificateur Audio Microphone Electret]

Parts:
C1: 2.2uF; C_0805_2012Metric_Pad1.18x1.45mm_HandSolder
C2, C8: 1uF; C_0805_2012Metric_Pad1.18x1.45mm_HandSolder
C3, C9: 0.1uF; C_0805_2012Metric_Pad1.18x1.45mm_HandSolder
C4: 10pF; C_0805_2012Metric_Pad1.18x1.45mm_HandSolder
C5, C7: 100pF; C_0805_2012Metric_Pad1.18x1.45mm_HandSolder
C6: 22nF; C_0805_2012Metric_Pad1.18x1.45mm_HandSolder
D1, D2, D3, D4: D_Zener; D_SOD-123
J1: Conn_MB; PinSocket_1x05_P2.00mm_Vertical
MK1: Micro; PinSocket_1x02_P2.00mm_Vertical
R1: 10k; R_0805_2012Metric_Pad1.20x1.40mm_HandSolder
R2, R3: 100k; R_0805_2012Metric_Pad1.20x1.40mm_HandSolder
R4: 75k; R_0805_2012Metric_Pad1.20x1.40mm_HandSolder
R5, R7: 47k; R_0805_2012Metric_Pad1.20x1.40mm_HandSolder
R6, R8: 51; R_0805_2012Metric_Pad1.20x1.40mm_HandSolder
U1: TL072; SOT-23-8_Handsoldering

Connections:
5V: D1.1 (K), D3.1 (K), J1.2
10V: C8.2, C9.2, J1.3, R1.1, R2.1, U1.8 (V+)
GND: C2.1, C3.1, C5.2, C7.1, C8.1, C9.1, D2.2 (A), D4.2 (A), J1.1, MK1.1 (-), R3.2, U1.4 (V-)
unnamed: C1.1, MK1.2 (+), R1.2
unnamed: C1.2, C4.1, R4.1, U1.2 (-)
unnamed: C2.2, C3.2, R2.2, R3.1, U1.3 (+), U1.5 (+)
unnamed: C4.2, R4.2, R5.1, R6.1, U1.1
unnamed: C5.1, C6.2, D1.2 (A), D2.1 (K), J1.5, R6.2
unnamed: C6.1, C7.2, D3.2 (A), D4.1 (K), J1.4, R8.2
unnamed: R5.2, R7.1, U1.6 (-)
unnamed: R7.2, R8.1, U1.7

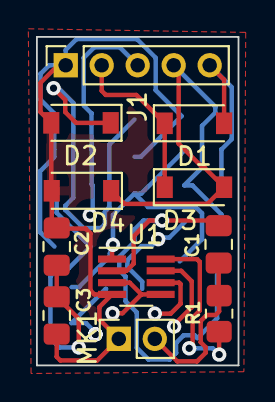
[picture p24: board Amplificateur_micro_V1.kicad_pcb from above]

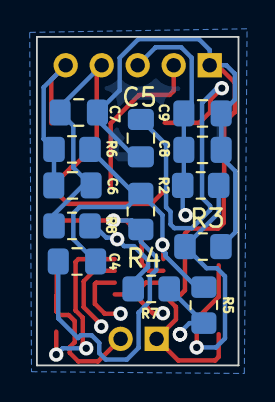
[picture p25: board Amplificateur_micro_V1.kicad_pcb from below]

Board: 4 copper layers, 11.2 x 18.2 mm, 24 parts (13 on the bottom side), 11 nets.

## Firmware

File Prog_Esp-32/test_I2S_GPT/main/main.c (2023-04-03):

#include "freertos/FreeRTOS.h"
#include "freertos/task.h"
#include "esp_system.h"
#include "esp_check.h"
#include <stdio.h>
#include <stdlib.h>
#include "esp_system.h"
#include "esp_log.h"
#include "driver/i2s.h"
#include "driver/sdmmc_host.h"
#include "driver/sdspi_host.h"
#include "driver/spi_common.h"
#include "sdmmc_cmd.h"
#include "sdkconfig.h"
#include "esp_vfs_fat.h"
#include <sys/unistd.h>
#include <sys/stat.h>
#include <stdio.h>
#include <string.h>
#include <math.h>
#include <stdint.h>
#include <rom/ets_sys.h>


#define I2S_NUM         I2S_NUM_0
#define I2S_Q_LEN       (8)
#define CHANNEL         (1)
#define SAMPLE_RATE     (44100)
#define BIT_WIDTH       (24)
#define I2S_NUM         (0)
#define I2S_READ_LEN    (1024)
#define PI 3.141592653589793  // value of pi
#define AMPLITUDE ((1<<23) -1)
#define SHIFT_BITS (8)

#define SPI_DMA_CHAN     SPI_DMA_CH_AUTO
#define SD_MOUNT_POINT      "/sdcard"
#define SD_CS           (GPIO_NUM_5)
#define SD_MOSI         (GPIO_NUM_23)
#define SD_CLK          (GPIO_NUM_18)
#define SD_MISO         (GPIO_NUM_19)
#define GPIO_I2S_WS     (GPIO_NUM_14)
#define GPIO_I2S_BCLK   (GPIO_NUM_13)
#define GPIO_I2S_DIN    (GPIO_NUM_12)

#define SAMPLE_RATE 44100
#define BIT_SAMPLE 24
#define NUM_CHANNELS 1
#define REC_TIME 1

#define WAV_HEADER_SIZE 44
#define SAMPLE_SIZE         (CONFIG_BIT_SAMPLE * 1024)   
#define BYTE_RATE           (SAMPLE_RATE * (BIT_SAMPLE / 8)) * NUM_CHANNELS 
size_t bytes_read;

sdmmc_host_t host = SDSPI_HOST_DEFAULT();
sdmmc_card_t *card;

static QueueHandle_t i2s_event_queue;

static const char *TAG = "i2s_GPT";

void mount_sdcard(void)
{
    esp_err_t ret;

    // Options for mounting the filesystem.
    // If format_if_mount_failed is set to true, SD card will be partitioned and
    // formatted in case when mounting fails.
    esp_vfs_fat_sdmmc_mount_config_t mount_config = {
#ifdef CONFIG_EXAMPLE_FORMAT_IF_MOUNT_FAILED
        .format_if_mount_failed = true,
#else
        .format_if_mount_failed = false,
#endif // EXAMPLE_FORMAT_IF_MOUNT_FAILED
        .max_files = 5,
        .allocation_unit_size = 16 * 1024
    };
    sdmmc_card_t *card;
    const char mount_point[] = SD_MOUNT_POINT;
    ESP_LOGI(TAG, "Initializing SD card");

    // Use settings defined above to initialize SD card and mount FAT filesystem.
    // Note: esp_vfs_fat_sdmmc/sdspi_mount is all-in-one convenience functions.
    // Please check its source code and implement error recovery when developing
    // production applications.
    ESP_LOGI(TAG, "Using SPI peripheral");

    sdmmc_host_t host = SDSPI_HOST_DEFAULT();
    spi_bus_config_t bus_cfg = {
        .mosi_io_num = SD_MOSI,
        .miso_io_num = SD_MISO,
        .sclk_io_num = SD_CLK,
        .quadwp_io_num = -1,
        .quadhd_io_num = -1,
        .max_transfer_sz = 4000,
    };
    ret = spi_bus_initialize(host.slot, &bus_cfg, SDSPI_DEFAULT_DMA);
    if (ret != ESP_OK) {
        ESP_LOGE(TAG, "Failed to initialize bus.");
        return;
    }

    // This initializes the slot without card detect (CD) and write protect (WP) signals.
    // Modify slot_config.gpio_cd and slot_config.gpio_wp if your board has these signals.
    sdspi_device_config_t slot_config = SDSPI_DEVICE_CONFIG_DEFAULT();
    slot_config.gpio_cs = SD_CS;
    slot_config.host_id = host.slot;

    ESP_LOGI(TAG, "Mounting filesystem");
    ret = esp_vfs_fat_sdspi_mount(mount_point, &host, &slot_config, &mount_config, &card);

    if (ret != ESP_OK) {
        if (ret == ESP_FAIL) {
            ESP_LOGE(TAG, "Failed to mount filesystem. "
                     "If you want the card to be formatted, set the CONFIG_EXAMPLE_FORMAT_IF_MOUNT_FAILED menuconfig option.");
        } else {
            ESP_LOGE(TAG, "Failed to initialize the card (%s). "
                     "Make sure SD card lines have pull-up resistors in place.", esp_err_to_name(ret));
        }
        return;
    }
    ESP_LOGI(TAG, "Filesystem mounted");

    // Card has been initialized, print its properties
    sdmmc_card_print_info(stdout, card);
    // Use POSIX and C standard library functions to work with files.
}

void generate_wav_header(char *wav_header, uint32_t wav_size, uint32_t sample_rate)
{
    // See this for reference: http://soundfile.sapp.org/doc/WaveFormat/
    uint32_t file_size = wav_size + WAV_HEADER_SIZE - 8;
    uint32_t byte_rate = BYTE_RATE;

    const char set_wav_header[] = {
        'R', 'I', 'F', 'F', // ChunkID
        //0x02, 0x04, 0xF0, 0x00, //ChunkSize
        file_size, file_size >> 8, file_size >> 16, file_size >> 24, // ChunkSize
        'W', 'A', 'V', 'E', // Format
        'f', 'm', 't', ' ', // Subchunk1ID
        0x10, 0x00, 0x00, 0x00, // Subchunk1Size (16 for PCM)
        0x01, 0x00, // AudioFormat (1 for PCM)
        0x01, 0x00, // NumChannels (1 channel)
        0x44, 0xAC, 0x00, 0x00, // SampleRate (44100)
        0xCC, 0x04, 0x02, 0x00, // ByteRate
        //byte_rate, byte_rate >> 8, byte_rate >> 16, byte_rate >> 24, // ByteRate
        0x03, 0x00, // BlockAlign 3 = 24 bit 1 channel ; 2 = 16 bit 1 channel
        0x18, 0x00, // BitsPerSample (0x18 = 24 bits) (0x10 = 16 bits)
        'd', 'a', 't', 'a', // Subchunk2ID
        //0x02, 0x04, 0xCC, 0x00, //Subchunk2Size
        wav_size, wav_size >> 8, wav_size >> 16, wav_size >> 24, // Subchunk2Size
    };

    memcpy(wav_header, set_wav_header, sizeof(set_wav_header));
}

void i2s_setup() {
    ESP_LOGI(TAG, "Initializing I2S");
    //int i = 0;
    /*unsigned int i2s_read_len = I2S_READ_LEN;
    size_t bytes_read = 0;
    int i2s_read_buff[i2s_read_len];*/
    i2s_config_t i2s_config = {
        .mode = I2S_MODE_SLAVE | I2S_MODE_RX,
        .sample_rate = SAMPLE_RATE,
        .bits_per_sample = BIT_WIDTH,
        .channel_format = I2S_CHANNEL_FMT_ONLY_LEFT,
        .communication_format = I2S_COMM_FORMAT_I2S | I2S_COMM_FORMAT_I2S_MSB,
        .intr_alloc_flags = ESP_INTR_FLAG_LEVEL1,
        .dma_buf_count = 3,
        .dma_buf_len = 1024,
    };
    i2s_pin_config_t pin_config = {
        .bck_io_num = GPIO_I2S_BCLK,
        .ws_io_num = GPIO_I2S_WS,
        .data_in_num = GPIO_I2S_DIN,
        .data_out_num = I2S_PIN_NO_CHANGE
    };
    i2s_driver_install(I2S_NUM, &i2s_config, I2S_Q_LEN, &i2s_event_queue);
    i2s_set_pin(I2S_NUM, &pin_config);
    /*
    while (1) {
        i = 0;
        if((i2s_read(I2S_NUM, (void *)i2s_read_buff, i2s_read_len, &bytes_read, portMAX_DELAY)) ==ESP_OK)
        {
            ESP_LOGI(TAG, "[echo] %d byte.", bytes_read);
            while(i < (1024/4))
            {
                ESP_LOGI(TAG, "Data du buffer position %d: %d", i, (int)i2s_read_buff[i]);
                i++;
            }
        }
            
        // process received data
        else
            ESP_LOGI(TAG,"ERROR");
        
    }
    */
}

void app_main() {
    //xTaskCreate(i2s_task, "i2s_task", 8198, NULL, 5, NULL);
    mount_sdcard();
    i2s_setup();

    // Use POSIX and C standard library functions to work with files.
    uint32_t rec_time = REC_TIME;
    int flash_wr_size = 0;
    ESP_LOGI(TAG, "Opening file");

    char wav_header_fmt[WAV_HEADER_SIZE];
    uint32_t flash_rec_time = BYTE_RATE * rec_time;
    generate_wav_header(wav_header_fmt, flash_rec_time, SAMPLE_RATE);

    ESP_LOGI(TAG, "Generating WAV header");
    // First check if file exists before creating a new file.
    struct stat st;
    if (stat(SD_MOUNT_POINT"/record.wav", &st) == 0) {
        // Delete it if it exists
        unlink(SD_MOUNT_POINT"/record.wav");
    }

    ESP_LOGI(TAG, "WAV file verification");
    // Create new WAV file
    FILE *f = fopen(SD_MOUNT_POINT"/record.wav", "wb"); //a (append) before now wb (new file and treat it as binary)
    if (f == NULL) {
        ESP_LOGE(TAG, "Failed to open file for writing");
        return;
    }

    ESP_LOGI(TAG, "Creating WAV file in SD card");
    // Write the header to the WAV file
    fwrite(wav_header_fmt, 1, WAV_HEADER_SIZE, f);
    ESP_LOGI(TAG, "Finished writing WAV file header");




	// Allocate DMA buffers
	size_t buf_size = 1024 * sizeof(int32_t);
	int32_t *dma_buf = (int32_t *)heap_caps_malloc(buf_size, MALLOC_CAP_DMA);
    int32_t *buf_ptr = (int32_t*) dma_buf;
    int32_t shiftValue = 0x00FF << SHIFT_BITS; // create the shift value

    
	if (!dma_buf) {
		ESP_LOGE(TAG, "Failed to allocate DMA buffer");
		fclose(f);
		return;
	}
    ESP_LOGI(TAG, "Allocating DMA buffer");
    //Code tester carte SD et format WAV ainsi que décalage 8bit vers la gauche
    size_t bytes_written = 0;

    
    //génération d'onde carré
    double t = 0;
    double sin_value = 0;
    int32_t sample = 0;
    int i = 0;
    while (flash_wr_size < flash_rec_time) {
        t = (double)i / SAMPLE_RATE;
        sin_value = sin(2.0 * PI * 1000.0 * t); // 1 kHz sine wave
        if(i% 500 == 0)
            sample = 0;//(uint32_t)(AMPLITUDE * sin_value) & 0xFFFFFF; // convert to 24-bit unsigned integer
        if(i% 1500 == 0)
            sample = 0x000FFFFF;//(uint32_t)(AMPLITUDE * sin_value) & 0xFFFFFF; // convert to 24-bit unsigned integer 
        //ESP_LOGI(TAG, "Generation d'onde sinus : %d", (int)sample);
        dma_buf[i%1024] = sample;
        //bytes_written += fwrite(sample, 4, 1, f);
        flash_wr_size += 4;
        i++;
        if(i%1024 == 0)
        {
            printf("dma_buf 0: %lu\r\n", dma_buf[0]);
            printf("dma_buf 1: %lu\r\n", dma_buf[1]);
            
            for (int j = 0; j < 1024; j++) {
               dma_buf[j] <<= SHIFT_BITS;
            }
            printf("dma_buf 0: %lu\r\n", dma_buf[0]);
            printf("dma_buf 1: %lu\r\n", dma_buf[1]);
            
            //bytes_written += fwrite(dma_buf, 1024, 4, f);
        }
            
    }
    bytes_written += fwrite(dma_buf[0], 4, 1, f);
    ets_delay_us(1000);			//Stalls execution for #uS
    bytes_written += fwrite(dma_buf[1], 4, 1, f);
    ets_delay_us(1000);			//Stalls execution for #uS
    bytes_written += fwrite(dma_buf[2], 4, 1, f);
    ets_delay_us(1000);			//Stalls execution for #uS
    bytes_written += fwrite(dma_buf[3], 4, 1, f);
    ets_delay_us(1000);			//Stalls execution for #uS
    bytes_written += fwrite(dma_buf[4], 4, 1, f);
    ets_delay_us(1000);			//Stalls execution for #uS


    //Code enregistrement audio du PCM
     /*
	// Receive and write audio data to file
	size_t bytes_written = 0;
    //QueueHandle_t i2s_event_queue = i2s_get_event_queue(I2S_NUM_0);
	while (flash_wr_size < flash_rec_time) {
		// Receive audio data
		i2s_event_t evt;
		if (xQueueReceive(i2s_event_queue, &evt, portMAX_DELAY)) {
			if (evt.type == I2S_EVENT_RX_DONE) {
				i2s_read(I2S_NUM, (char *)dma_buf, buf_size, &bytes_read, portMAX_DELAY);
				flash_wr_size += bytes_read;

				// Write audio data to file
				if (bytes_read > 0) {
					size_t bytes = fwrite(dma_buf, 1, bytes_read, f);
					bytes_written += bytes;
				}
			}
		}
        
        flash_wr_size += bytes_read;
	}
    */
    ESP_LOGI(TAG, "Finished writing AUDIO into file");

	// Update WAV header with total data size
    ESP_LOGI(TAG, "total bytes to write = %d", flash_wr_size);
    ESP_LOGI(TAG, "Nomber of bytes written = %d", bytes_written);

    ESP_LOGI(TAG, "Closing file");
	fclose(f);
    //esp_vfs_fat_sdcard_unmount(SD_MOUNT_POINT, card);
    return;
}

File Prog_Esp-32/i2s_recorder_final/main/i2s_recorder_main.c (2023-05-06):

/**
 * @file   i2s_recorder_main.c
 * @author Eric Gingras, Jacob Turcotte
 * @date  5 mai 2023
 * @brief Ce programme utilise un microcontrôleur ESP-32 pour enregistré des données audio provenant 
 * d'un ADC à l'aide du protocole I2S. Les données sont ensuite stockées sur une carte SD. Lorsque le 
 * programme est exécuté, il est en attente d'un signal d'interruption du bouton d'enregistrement. 
 * Lorsque le bouton est appuyé pour la première fois, le programme monte la carte SD,initialise le canal 
 * I2S et commence à enregistrer des données audio. Les données sont stockées sur la carte SD dans un fichier 
 * de format WAV. Lorsque le bouton est appuyé une deuxième fois, l'enregistrement s'arrête et le fichier est fermé.   
 * 
 */


/************************* INCLUDES *************************/

#include <stdio.h>
#include <string.h>
#include <math.h>
#include <sys/unistd.h>
#include <sys/stat.h>
#include <pthread.h>
#include "esp_log.h"
#include "esp_err.h"
#include "esp_system.h"
#include "esp_vfs_fat.h"
#include "freertos/FreeRTOS.h"
#include "freertos/task.h"
#include "freertos/queue.h"
#include "driver/i2s_std.h"
#include "driver/gpio.h"
#include "driver/spi_common.h"
#include "sdmmc_cmd.h"
#include "sdkconfig.h"


/************************* CONSTANTES *************************/

#define SPI_DMA_CHAN        SPI_DMA_CH_AUTO
#define NUM_CHANNELS        1 // For mono recording only!
#define SD_MOUNT_POINT      "/sdcard"
#define SAMPLE_SIZE         1024
#define BYTE_RATE           (CONFIG_SAMPLE_RATE * (CONFIG_BIT_SAMPLE / 8)) * NUM_CHANNELS
#define BUTTON_PIN 25
#define LED_PIN 33
#define MAX_FILENAME_LEN  32

/************************* VARIABLES GLOBALES *************************/

static const char *TAG = "pcm_recorder";

const int WAVE_HEADER_SIZE = 44;
int32_t i2s_readraw_buff[SAMPLE_SIZE];
size_t bytes_read;

// When testing SD and SPI modes, keep in mind that once the card has been
// initialized in SPI mode, it can not be reinitialized in SD mode without
// toggling power to the card.
sdmmc_host_t host = SDSPI_HOST_DEFAULT();
sdmmc_card_t *card;
i2s_chan_handle_t rx_handle = NULL;

static int button_press_count = 0;
char folder_path[MAX_FILENAME_LEN];
char file_path[MAX_FILENAME_LEN + 32]; // Extra characters for "/record.wav"

static volatile bool is_recording = false; // Variable that dictates whether the program is recording audio data or not
QueueHandle_t interputQueue;


/************************* PROTOTYPES *************************/

void mount_sdcard(void);
void init_i2s_driver(void);
void record_wav(void*);


/*
 * @brief Gestionnaire d'interruptions de GPIO
 * @param *args: pointeur vers les arguments de la fonction
 * @return IRAM_ATTR: attribut pour stocker la fonction dans la RAM interne
 */
static void IRAM_ATTR gpio_interrupt_handler(void *args)
{
    int pinNumber = (int)args; // Get GPIO number
    xQueueSendFromISR(interputQueue, &pinNumber, NULL); // Send pin number to interrupt queue
}
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

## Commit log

2023-01-19 commit de documentation
2023-01-19 document session 1 pcb
    [Prototype_vers_de_terre_2.kicad_pcb, Prototype_vers_de_terre_2.kicad_sch]
2023-01-19 Ajout du dossier de l'interface ordi
2023-01-26 Terminer PCB ampli audio
    [Amplificateur_micro_V1.kicad_pcb, Amplificateur_micro_V1.kicad_sch]
2023-01-26 Excel de liste de pièce
    [Liste_piece_commande_1.xlsx]
2023-01-30 Ajout des descriptions de fichiers dans le README
2023-02-09 Ajout du fichier arduino pour le pcm1804
2023-02-09 Upload du fichier kicad pour le pcm1804
    [PCM1804.kicad_pcb, PCM1804.kicad_sch]
2023-02-09 kicad pour pcm1804 version 1 fini
    [PCM1804.kicad_sch]
2023-03-14 Kicad, PA et site web
    [9V_alim.kicad_sch, ESP-32.kicad_sch, Ecout-Terre_PCB_V1.csv, Ecout-Terre_PCB_V1.xlsx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]
2023-03-20 Trace pcb
    [9V_alim.kicad_sch, ESP-32.kicad_sch, Ecout-Terre_PCB_V2.kicad_pcb, Ecout-Terre_PCB_V2.kicad_sch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]
2023-04-03 Ajout de la version plus récente du code pour la lecture I2S qui sauvegarde à la carte SD
2023-04-03 Envoie de code et correction PCB
    [9V_alim.kicad_sch, ESP-32.kicad_sch, Ecout-Terre_PCB_V1.kicad_pcb, Ecout-Terre_PCB_V2.csv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]
2023-04-03 Ajout de pièces 3d
    Pièce qui va dans la bas du boîtier. Le PCB sera vissé dessus
    [Base_v1_boitier.f3d, boitierv1 v2.stl]
2023-04-03 Modification du Readme
    Ajout de description du code ainsi que des instructions d'utilisation
2023-04-04 changement de png à jpg pour le schéma synoptique
2023-04-04 Mauvais fichier de lecture I2S remplacé avec le bon
2023-04-17 Répertoire + fichier zip kicad
    Fichier .zip kicad pour envoyer à JLCPCB
    Nouveau répertoire pour créer procédure de setup
2023-05-01 Clarification du schéma pcb
    [9V_alim.kicad_sch, Ecout-Terre_PCB_V2.kicad_pcb, audio.kicad_sch]
2023-05-01 Ajout de génération de fichier
    Crée un fichier enregistrement'N' où N est égal au nombre d'enregistrement. Besoin de faire une gestion des doublons
2023-05-01 Gestion DEL, gestion fichier doublon, correction schéma électrique
    PIN 23 à côté de la PIN 25 est en fait la PIN 33.
    Gestion de DEL pour qu'elle flash au quart de seconde.
    Gestion de doublon de fichier afin que l'application crée un nouveau fichier selon le nombre de fichier déjà existant. (aucun écrasement)
2023-05-05 Suppression du déscription du répertoire Arduino
2023-05-05 ajout de commentaire
2023-05-06 Ajout de commentaires au code I2S
